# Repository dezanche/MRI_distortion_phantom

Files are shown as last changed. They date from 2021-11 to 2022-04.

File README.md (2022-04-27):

# MRI Distortion Phantom

This modular phantom uses solid signal sources to measure distortion in magnetic resonance imaging (MRI) systems. Its large volume and light weight make it practical for applications such as radiation therapy where accurate patient contours are critical for treatment planning. Please note that image distortion can depend on variables such as sequence parameters and magnetic field (B<sub>0</sub>) homogeneity.
This repository contains detailed information in addition to the scientific abstract presented at the [2022 ISMRM conference](https://www.ismrm.org/22m/) (#5032).
  
## Contents
[CAD](https://github.com/dezanche/MRI_distortion_phantom/blob/main/CAD) contains CAD files describing the phantom as built.\
[Images](https://github.com/dezanche/MRI_distortion_phantom/blob/main/Images) contains screenshots and photographs.\
[Support_files](https://github.com/dezanche/MRI_distortion_phantom/blob/main/Support_files) contains software and other files used for processing data obtained with the phantom.\
[Construction](#construction) describes how the phantom is designed and built.\
Images acquired using the phantom can be processed to analyze the distortion using both [3D Slicer](#data-processing-using-3d-slicer) and [Matlab](#data-processing-using-matlab).

## Construction
The phantom is made using off-the-shelf parts as much as possible. The [CAD](https://github.com/dezanche/MRI_distortion_phantom/blob/main/CAD) drawing was made in [FreeCAD](https://www.freecad.org/) and includes all elements of the phantom as built. Parameters in the table included in the file can be changed to adapt the model to different dimensions.\
The proton signal is generated by silicone rubber beads (9 mm ⌀ spheres with a 2 mm ⌀ axial hole for mounting), attached to a support structure using M2 nylon screws and nuts.
The support structure consists of stacked polypropylene sheets, 3.3 mm thick and with 4 mm ⌀ holes at regular intervals (25.4 mm “peg board”). The sheets are joined using nylon threaded rods and separated by stand-offs 22.1 mm in height, resulting in a 3-dimensional grid with isotropic pitch.
The present configuration uses 11 sheets with 11⨉18 holes, for a possible 2178 sample locations.
Slotted side panels can be added to increase flexural, torsional, and shear stiffness.
Three rows from the edges of the boards were populated with 1386 beads to allow a 25 mm ⌀ container filled with ~12 mL of petroleum jelly to be placed at the centre of the phantom for automatic flip angle and frequency calibration. More positions can be populated if desired.\
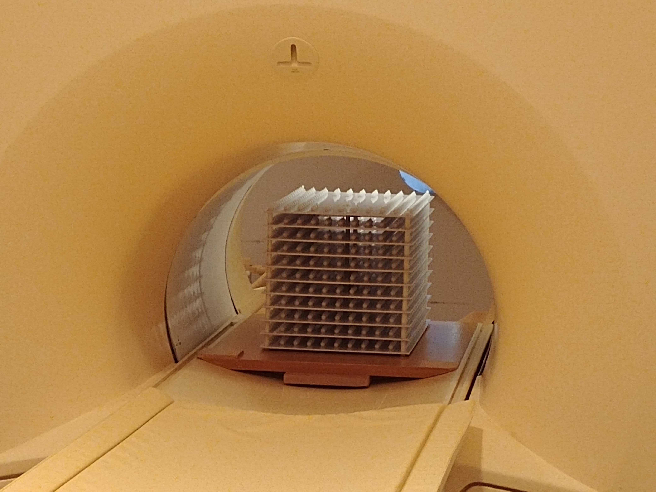
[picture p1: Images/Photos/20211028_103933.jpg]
scanner

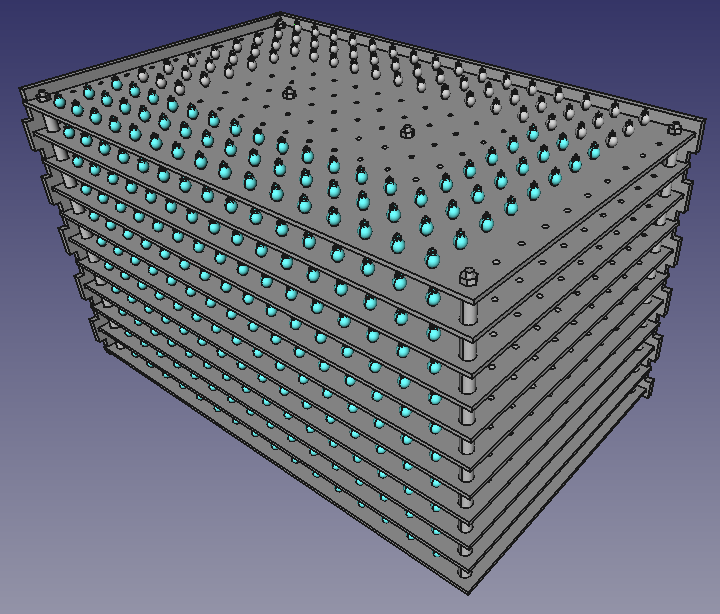
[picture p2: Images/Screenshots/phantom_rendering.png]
rendering


## Data Processing Using 3D Slicer 

After scanning the volume occupied by the phantom, export the volume in DICOM format and analyze in [3D Slicer](https://www.slicer.org/) as follows.

### 1. Data Import
- DICOM browser module: select series and load
- Volume rendering module: display preset > MRI MIP > adjust "shift" to see cloud of dots
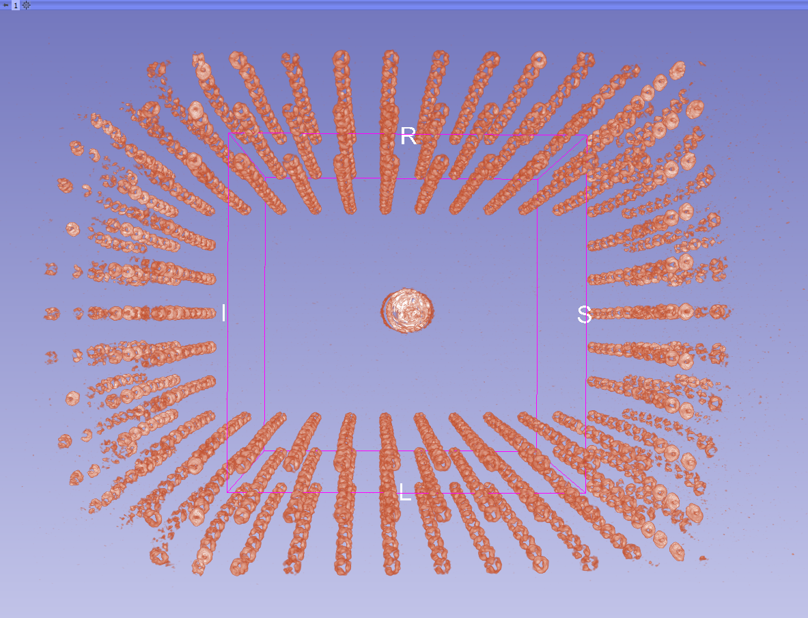
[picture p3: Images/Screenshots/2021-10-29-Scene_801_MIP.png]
MIP


### 2. Segment
- Segment editor module: add segment > threshold > set threshold* > apply > show 3D \
(adjust low range of threshold while viewing RGY screens: start high and lower it to see beads but minimize noise and artefacts) \
then clean up using
- Segment editor module: islands > Split islands to segments> set min size > apply \
(e.g., min size 50 voxels)
- (optional) clean up manually by excluding segments corresponding to, e.g., noise, artefacts, central sample, etc.
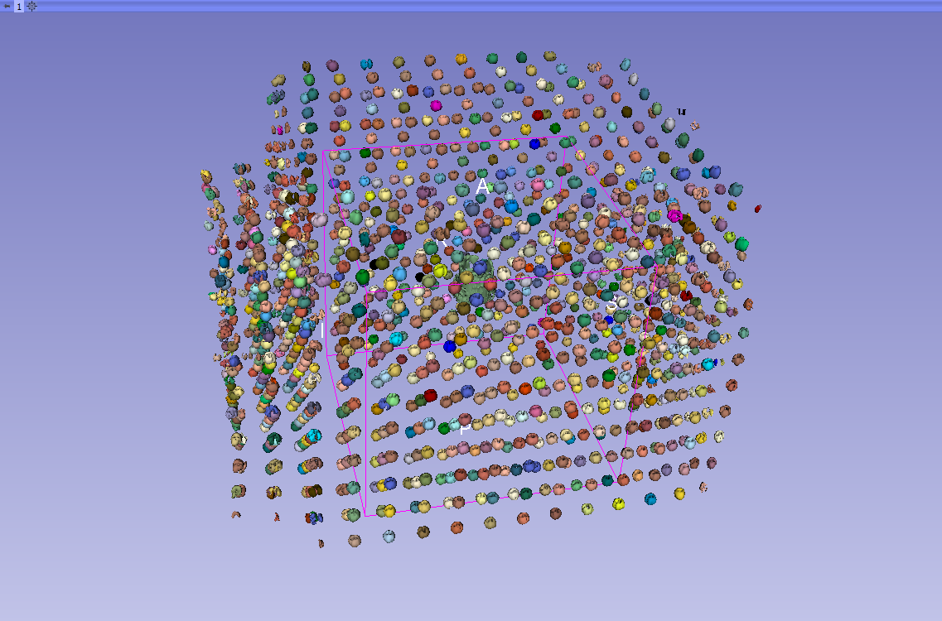
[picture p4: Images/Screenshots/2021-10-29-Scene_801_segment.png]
segmentation


### 3. Calculate Centroid of Each Segment
- following the methods in (https://discourse.slicer.org/t/centroid-determination/3541) copy and paste the following code into Slicer's Python Interactor:
```python
segmentationNode = getNode("Segmentation")  # or whatever name was given to the segmentation
# Compute centroids
import SegmentStatistics
segStatLogic = SegmentStatistics.SegmentStatisticsLogic()
segStatLogic.getParameterNode().SetParameter("Segmentation", segmentationNode.GetID())
segStatLogic.getParameterNode().SetParameter("LabelmapSegmentStatisticsPlugin.centroid_ras.enabled", str(True))
segStatLogic.computeStatistics()
stats = segStatLogic.getStatistics()
# Place a markup point in each centroid
markupsNode = slicer.mrmlScene.AddNewNodeByClass("vtkMRMLMarkupsFiducialNode")
markupsNode.CreateDefaultDisplayNodes()
for segmentId in stats["SegmentIDs"]:
  centroid_ras = stats[segmentId,"LabelmapSegmentStatisticsPlugin.centroid_ras"]
  segmentName = segmentationNode.GetSegmentation().GetSegment(segmentId).GetName()
  markupsNode.AddFiducialFromArray(centroid_ras, segmentName)
```
  
- lock markups corresponding to centroids so they can't be accidentally moved with the mouse:\
Markups module > Control Points > Interaction in Views > lock
- uncheck *Point Labels* under *Advanced* to view the cloud of fiducials without labels cluttering the scene

### 4. Import Known Grid Positions
- create an FCSV file containing the XYZ coordinates of all beads in the phantom using `bead_coordinates.m' or other means (see the [Markups module documentation](https://www.slicer.org/wiki/Documentation/4.10/Modules/Markups) and https://discourse.slicer.org/t/convert-csv-files-to-be-loadable-as-fiducials-or-as-sequence-of-fiducials-json/18320/2)
- load the FCSV file directly from UI using “Add data” dialog
- lock markups corresponding to beads so they can't be accidentally moved with the mouse:\
Markups module > Control Points > Interaction in Views > lock

### 5. Manual Alignment
If some rotation and translation are needed to align the 2 sets of fiducials proceed as follows:
- Data module > right-click “Transform” column (on the beads coordinates) > Create new transform
- right-click Transform > Edit properties...
- adjust translation and rotation sliders to get the 2 sets aligned
- to make the changes permanent: Data module > Transform hierarchy tab > right click on the transform > "harden transform"
- save transformed coordinates to FCSV file if desired
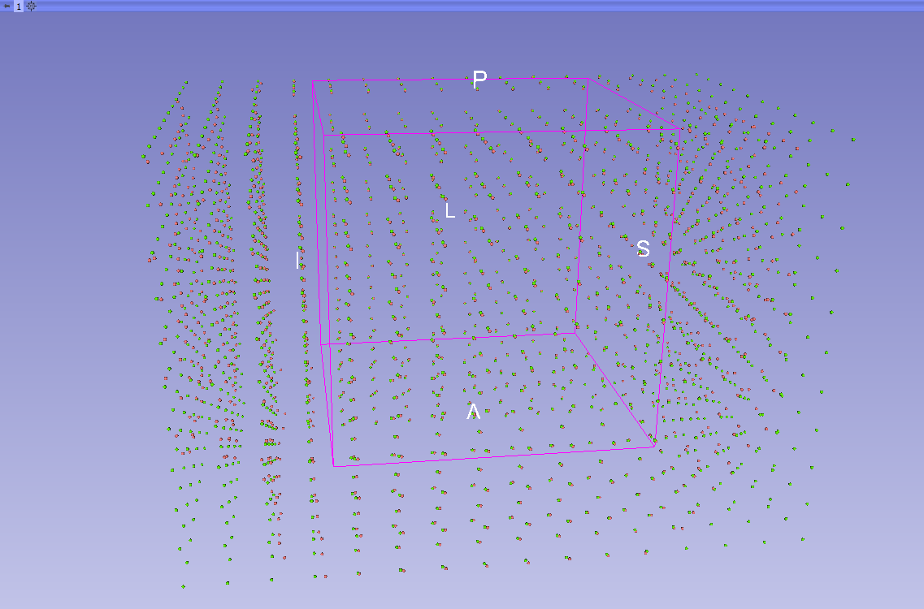
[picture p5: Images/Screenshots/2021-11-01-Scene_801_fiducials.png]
fiducials


### 6. Calculate Displacements
The following code (paste into Slicer's Python Interactor) calculates displacements between each measured centroid and the corresponding known coordinates, discards pairs more than `maxDistance` apart, and writes the results in a table.
```python
import scipy
import numpy as np
from scipy.spatial import KDTree
from scipy.spatial.distance import cdist
print('finding nearest neighbour pairs...\n')

maxDistance = 20;   #distance beyond which points are ignored [mm]

knownPointsNode = getNode('bead_coordinates');   # known points 3D Slicer node
queryPointsNode = getNode('MarkupsFiducial');   # query points 3D Slicer node

knownPoints = slicer.util.arrayFromMarkupsControlPoints(knownPointsNode);     # fiducials of known grid points
queryPoints = slicer.util.arrayFromMarkupsControlPoints(queryPointsNode);    # fiducials of measured centroids

# create the k-dimensional tree from the known points:
tree = KDTree(knownPoints);

# query the tree with the query points using upper bound maxDistance:
distances, indices = tree.query(queryPoints, k=1, distance_upper_bound=maxDistance);

print('minimum distance =', min(distances), ' \n')

# select pairs that are not assigned inf distance
nearIndices = indices[np.isfinite(distances)];
nearQueryPoints = queryPoints[np.isfinite(distances)];
reorderedKnownPoints = np.take(knownPoints,nearIndices,axis = 0);
distanceMatrix = cdist(nearQueryPoints,reorderedKnownPoints);
reorderedDistances = distanceMatrix.diagonal();

radialCoordinate = np.linalg.norm(reorderedKnownPoints, axis=1);

print('maximum distance =', max(reorderedDistances), ' \n')

# write result into table; see https://www.slicer.org/wiki/Documentation/4.10/ScriptRepository#Create_histogram_plot_of_a_volume
tableNode=slicer.mrmlScene.AddNewNodeByClass("vtkMRMLTableNode")
tableNode.SetName('Coordinates and Displacements')
updateTableFromArray(tableNode, np.hstack((nearQueryPoints, reorderedKnownPoints, np.vstack((radialCoordinate, reorderedDistances)).T, np.absolute(reorderedKnownPoints-nearQueryPoints))),["actual X","actual Y","actual Z","grid X","grid Y","grid Z","rho","displacement","|dX|","|dY|","|dZ|"]);

# launch pop-up table
tableView=slicer.qMRMLTableView()   
tableView.setMRMLTableNode(tableNode)
tableView.show()
```
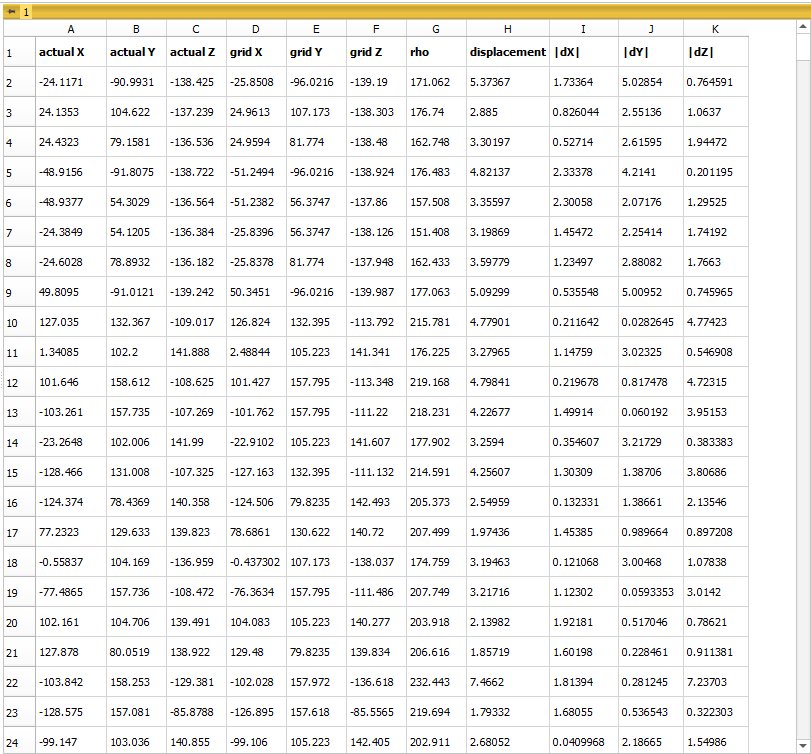
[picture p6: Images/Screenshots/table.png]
table


### 7. Plot Results
The data in the table can be saved to a TSV file and analyzed using other software, or plotted directly in 3D Slicer as follows.
- Plots module > Charts tab > Create New Plotchart, Create New Plotseries
- Series tab > select Data Series, Plot Type > Scatter, Input Table > Coordinates and Displacements
- choose X and Y Axis columns (e.g., the radial coordinate *rho* and *displacement* magnitude, respectively, in the example below)
- Line Style > none
- if not visible, display the plot window by clicking the eye in the Charts tab\
or main menu: View > Layout > 3D Table
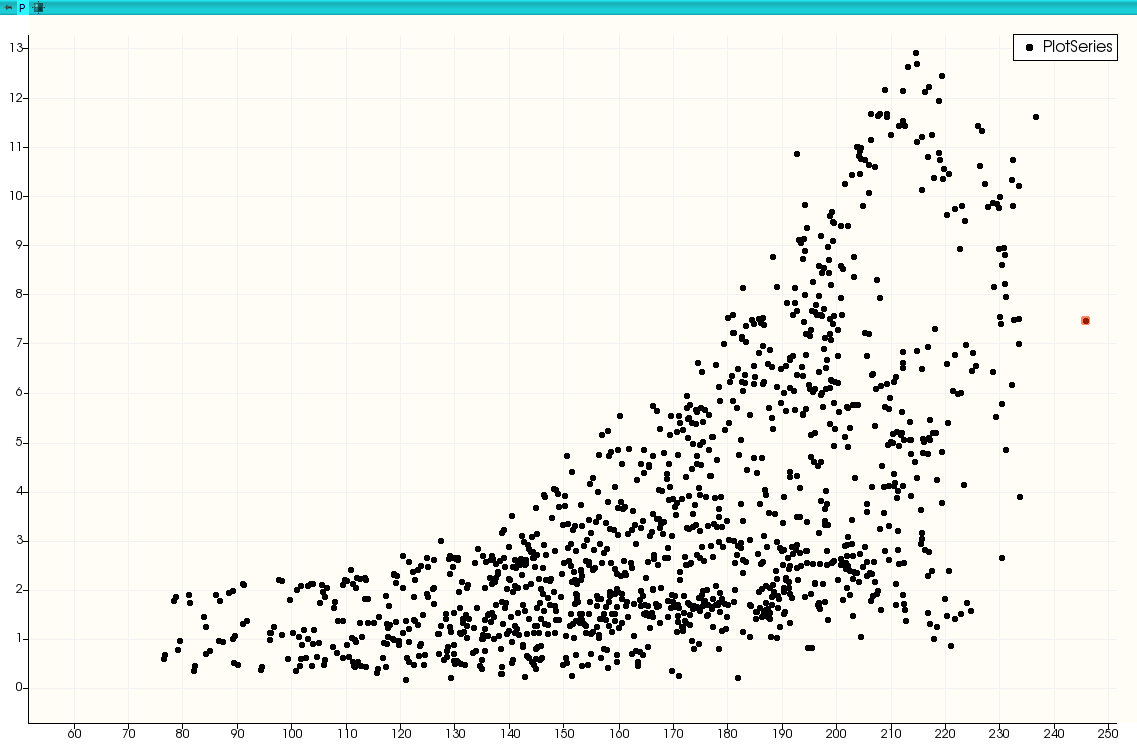
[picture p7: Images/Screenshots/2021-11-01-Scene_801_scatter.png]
scatter


## Data Processing Using Matlab
The acquired data can also be processed in Matlab using [Distortion_Analysis.m](./blob/main/Support_files/Distortion_Analysis.m).
Please note that this code will not run in [GNU Octave](https://www.gnu.org/software/octave/) because a couple of critical functions used in the script are not available in Octave toolboxes.

## Contributors
Mariko Gardiner, Keith Wachowicz, and Nicola De Zanche.

## Licenses
[CAD](https://github.com/dezanche/preclinical_MRI_phantom/tree/main/CAD) files are licensed under the [CERN-OHL-W license](https://ohwr.org/cern_ohl_w_v2.pdf), version 2 or any later version. Additional license information is provided in that folder.\
Software code is licensed under the terms of the [GNU General Public License](https://www.gnu.org/licenses/gpl-3.0.en.html) as published by the Free Software Foundation, either version 3 of the License, or any later version.\
\
All other original content in this repository (including this README file) is licensed under a [Creative Commons Attribution-NoDerivatives 4.0 International License](https://creativecommons.org/licenses/by-nd/4.0/).

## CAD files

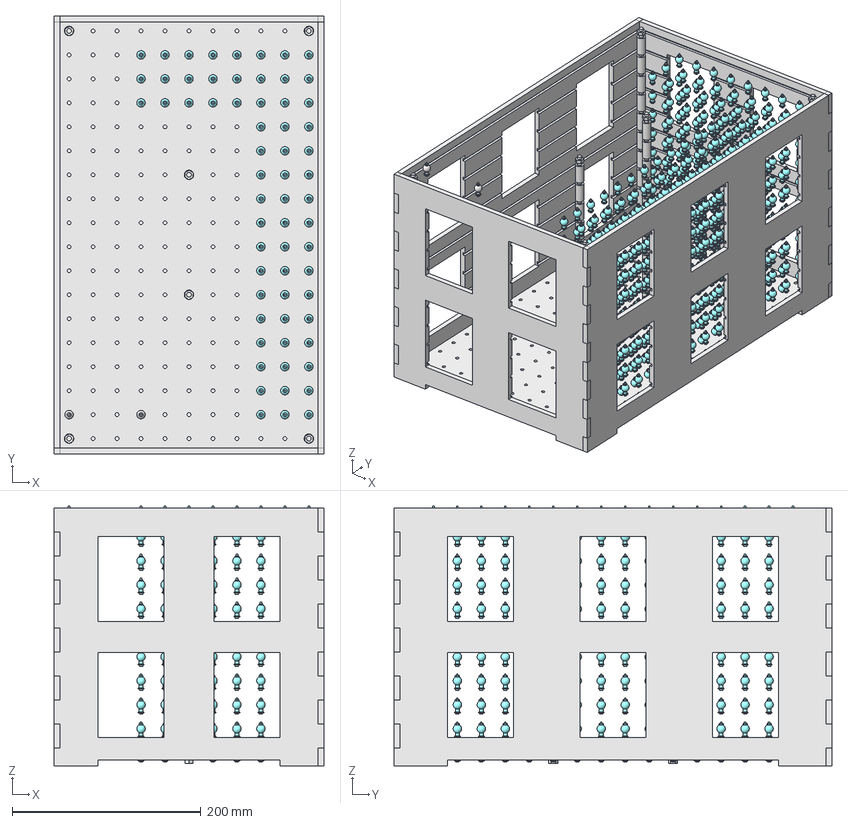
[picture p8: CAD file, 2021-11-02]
CAD/Silicone_Bead_Phantom.FCStd
286.0 x 463.6 x 275.3 mm
Short Side
Long Side
Long Side001
Short Side001
Spacer001
Threaded Rod
Top Nut
Bottom Nut
Corner001
Corner002
Corner003
Center01
Center02
ScrewAssy1
ScrewAssy002
Bead
Bead001
Bottom Board
